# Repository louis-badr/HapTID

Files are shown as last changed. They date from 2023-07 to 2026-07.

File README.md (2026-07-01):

# HapTID - Haptic Technology for Improved Dexterity

<p align="center">
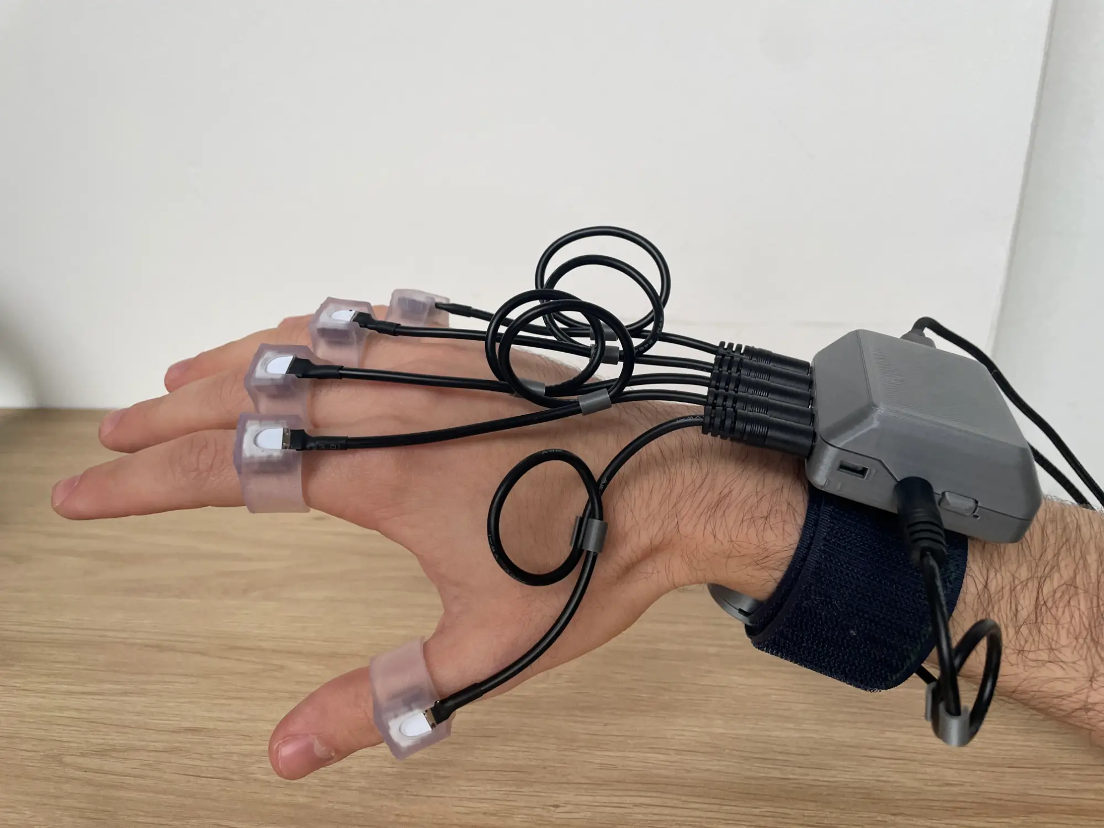
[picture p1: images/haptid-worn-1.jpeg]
HapTID device
  
</p>

HapTID is a study on how vibrotactile stimulation can improve manual dexterity in healthy subjects. In this repository you will find:

- Hardware :
    - The parts list and assembly guide of the device
    - CAD files for the 3D printed parts
    - Electronic schematics and PCB design files

- Software :
    - A pygame program for the study on healthy subjects
    - A script to generate the running order of the tasks and parameters for the study

- Firmware :
    - Arduino sketches for the study on healthy subjects
    - Arduino sketches to test motor vibrations using an accelerometer

You can also find a web interface to test the device at [https://louis-badr.fr/HapTID/](https://louis-badr.fr/HapTID/) and its source code in the `web_app` branch.

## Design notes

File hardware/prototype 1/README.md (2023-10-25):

# HapTID first hardware prototype

This folder contains the first hardware prototype of the HapTID project.
The design objectives of this prototype are:
- be able to produce sub-threshold vibrations on the wrist ranging from 0 to 500 Hz
- be able to produce supra-threshold vibrations on each finger
- be able to produce different signals simultaneously on all actuators
- has wired communication to reduce latency (this is an experimental prototype)

## Parts list
 
### 3D printed parts

The enclosures were printed with a Prusa i3 MK3S in PLA filament with 0.2 mm layer height and no supports.
The flexible rings can be casted in silicone with a 3D printed mold, here they were 3D printed with Formlabs Flexible 80A resin.
You can find the .step files in the `3D models` folder.

### Electronics

- Custom Prototype 1 PCB
- Generic ESP32 WROOM DevKit (38 pins)
- x6 2.5mm male audio jack connectors
- x6 VLV101040A motors by Vybronics
- x1 HD-VA3222 motor by PUI Audio

### Other parts

- A velcro strap (38mm wide here)
- x4 M2x8mm screws to secure the PCB

## Assembly guide

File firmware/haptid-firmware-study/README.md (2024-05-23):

# HapTID firmware

This is the Arduino sketch made to run for the study on healthy subjects (works with pygame_study_software).
The ESP32 listens to the serial port for a value:

- 0 to stop all vibrations

- between 1 and 100000 to control the noise level on output 1 (from 0.001% to 100%)

- between 100001 and 200000 to control the 80Hz tone level on ouput 3
- between 200001 and 300000 to control the 80Hz tone level on output 5
- between 300001 and 400000 to control the 250Hz tone level on output 3
- between 400001 and 500000 to control the 250Hz tone level on output 5

- between -1 and -100000 to control the click level on output 1
- between -100001 and -199999 to control the click level on output 2
- between -200001 and -299999 to control the click level on output 3
- between -300001 and -399999 to control the click level on output 4
- between -400001 and -499999 to control the click level on output 5
- between -500001 and -599999 to control the click level on output 6
- between -600001 and -699999 to control the click level for a click on all outputs at the same time

- between -700001 and -799999 to play a sine click on output 1
- between -800001 and -899999 to play a sine click on output 2
- between -900001 and -999999 to play a sine click on output 3
- between -1000001 and -1099999 to play a sine click on output 4
- between -1100001 and -1199999 to play a sine click on output 5
- between -1200001 and -1299999 to play a sine click on output 6

There is also a .wav file converter modified from https://github.com/rgrosset/pico-pwm-audio by Robin Grosset.

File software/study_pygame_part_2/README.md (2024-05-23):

# HapTID Study Part 2

## Goal: Assess the effects of sub-threshold wrist noise vibrations on reaction time

The main goal of this study is to assess the effects of wrist sub-threshold noise vibrations on reaction time.
The study is divided into three parts to:
1. Get the Stochastic Resonance (SR) vibration level by measuring the participant's Perception Threshold (PT) to noise at the wrist (set to 80% of the participant's PT)
2. Get the maximum finger vibration level (for confort) by assessing the participant's PT to 250Hz sinusoidal vibration on the index finger (set to 150% of the participant's PT)
3. Assess the effects of SR on reaction time with a Choice Reaction Time (CRT) task

## Setup
The participant is seated at a table in front of a computer screen, with the HapTID device installed on their non-dominant hand.
For the CRT task, each of their finger rests on a force sensitive button.
The participant wears earplugs to isolate them from the sounds the stimulators and the speaker can produce.

## Course of the study

### Perception Thresholds (approx. 6min)
To assess the participant's perceptual thresholds to different stimuli (1)(2), the double staircase method is used:
One after the other, a stimulus is emitted by the HapTID device.
The participant is asked to indicate whether or not they perceive the stimulus.
Depending on the response, the stimulus intensity is increased or decreased until a threshold is found.
Each assessment consists of a descending then ascending phase of stimulus intensity.

### Choice Reaction Time (CRT) task (33min45s without breaks)
The exercises are grouped by block according to the instructions (visual and/or tactile) and the presence or absence of sub-threshold wrist noise.
The exercises follow each other every 3 seconds.
The participant must press a key to continue, and can therefore take a break, every 25 exercises.
The course of the study is as follows:

1. Block without noise (sub-blocks in random order)(9x5x5x3 = 11min15s minimum):
    - No WS, visual IS, 5 repetitions per finger (random order)
    - No WS, tactile IS (click), 5 repetitions per finger (random order)
    - No WS, tactile IS (vibration), 5 repetitions per finger (random order)
    - Visual WS, visual IS, 5 repetitions per finger (random order)
    - Visual WS, tactile IS (click), 5 repetitions per finger (random order)
    - Visual WS, tactile IS (vibration), 5 repetitions per finger (random order)
    - Tactile WS (click), visual IS, 5 repetitions per finger (random order)  
    - Tactile WS (click), tactile IS (click), 5 repetitions per finger (random order)
    - Tactile WS (click), tactile IS (vibration), 5 repetitions per finger (random order)

2. Block with noise (sub-blocks identical to block 1 in random order)(11min15s minimum)

3. Control block without noise (sub-blocks identical to block 1 in random order)(11min15s minimum)

(WS: Warning Signal, IS: Imperative Signal)

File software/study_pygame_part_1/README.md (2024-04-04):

# HapTID Study Part 1

## Objectives
1. Get the Stochastic Resonance (SR) volume level by assessing the participant's perception threshold to white noise at the wrist
2. Assess the effects of SR on sensitivity (index finger) to
    1. 80Hz sinusoidal vibration
    2. 250Hz sinusoidal vibration
    3. Clicks

## Setup
The participant is seated at a table in front of a computer screen, with the HapTID device installed on his non-dominant hand. Their index finger rests on the surface of a bone-conduction audio speaker. The participant wears earplugs to isolate them from the sounds the stimulators and the speaker can produce.

## Course of the study
The study aims to assess the participant's perceptual thresholds to different stimuli.
The double staircase method is used: One after the other, a stimulus is emitted by the HapTID device or by the bone conduction loudspeaker. The participant is asked to indicate whether or not they perceive the stimulus. Depending on the response, the stimulus intensity is increased or decreased until a threshold is found. Each assessment consists of a descending then ascending phase of stimulus intensity.
Assessments are performed in the following order:
1. Assessment of white noise perception threshold on the wrist
2. Assessment of perception threshold on index finger without SR to (random order for each participant):
    - 80Hz sinusoidal vibration
    - 250Hz sinusoidal vibration
    - Clicks
3. Assessment of perception threshold on index finger with SR to (same order as previous assessment):
    - 80Hz sinusoidal vibration
    - 250Hz sinusoidal vibration
    - Clicks
4. Assessment of perception threshold on index finger without SR to (same order as previous assessment):
    - 80Hz sinusoidal vibration
    - 250Hz sinusoidal vibration
    - Clicks

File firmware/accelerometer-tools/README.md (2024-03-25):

# Accelerometer Sketches

The aim of using an accelerometer with vibration motors is to:
- Verify the latency of the system
- Analyze and equalize the frequency response of the motors

## Wiring

Using the ADXL345 accelerometer:

- VCC -> 3.3V
- GND -> GND
- X-OUT -> any input pin
- Y-OUT -> any input pin
- Z-OUT -> any input pin

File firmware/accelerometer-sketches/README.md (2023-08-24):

# Accelerometer Sketches

The aim of using an accelerometer with vibration motors is to:
- Verify the latency of the system
- Have the same vibration intensity for given frequencies

## Wiring

Using the ADXL345 accelerometer:

VCC -> 3.3V
GND -> GND
X-OUT -> any input pin
Y-OUT -> any input pin
Z-OUT -> any input pin

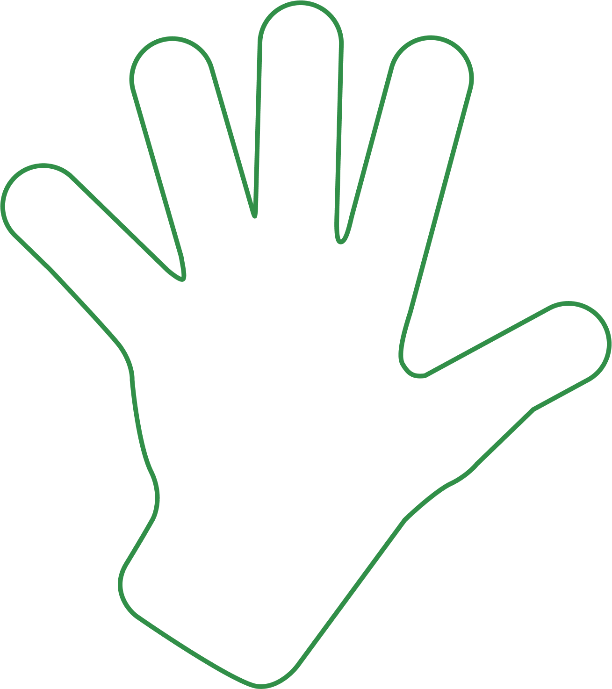
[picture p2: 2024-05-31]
software/study_pygame_part_2/hand_drawing_green.png

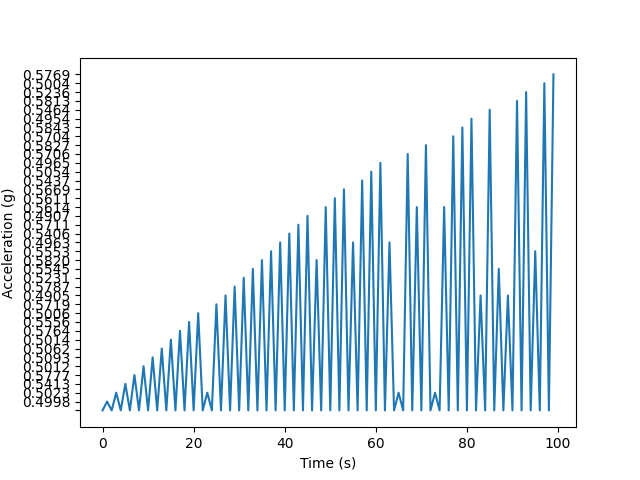
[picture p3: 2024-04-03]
firmware/accelerometer-tools/Figure_1.png

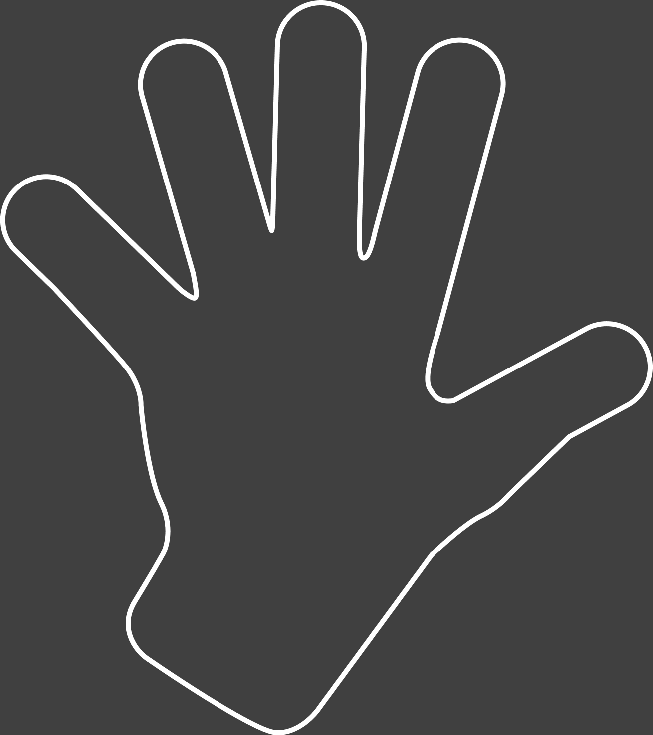
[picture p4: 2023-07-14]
software/study_pygame_part_2/hand_drawing.png

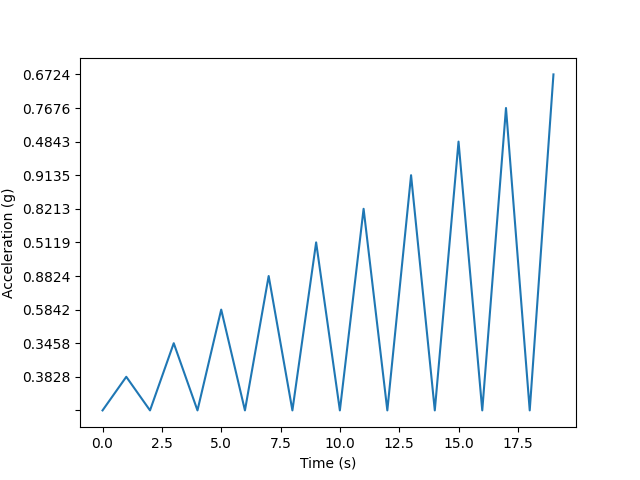
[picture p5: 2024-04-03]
firmware/accelerometer-tools/Figure_2.png

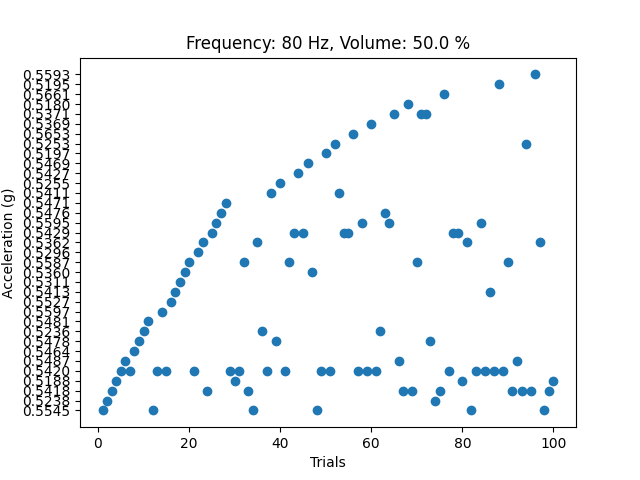
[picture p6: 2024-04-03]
firmware/accelerometer-tools/Figure_3.png

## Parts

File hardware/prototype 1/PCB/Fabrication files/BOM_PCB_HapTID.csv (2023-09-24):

ID | Name | Designator | Footprint | Quantity | Manufacturer Part | Manufacturer | Supplier | Supplier Part | Price
1 | PJ-2104-3A | #1,#2,#3,#4,#5,#6 | AUDIO-TH_PJ-2104-3A | 6 | PJ-2104-3A | Korean Hroparts Elec | LCSC | C707243 | 0.094
2 | 560 | R22 | R0603 | 1
3 | 300 | R23 | R0603 | 1
4 | KT-0603R | LED1 | LED0603-RD | 1 | KT-0603R | KENTO | LCSC | C2286
5 | 19-217/GHC-YR1S2/3T | LED2 | LED0603-RD | 1 | 19-217/GHC-YR1S2/3T | EVERLIGHT(亿光) | LCSC | C72043 | 0.027
6 | TYPE-C 6P(073) | USB1 | TYPE-C-SMD_TYPE-C-6P | 1 |  | SHOU HAN(首韩) | LCSC | C668623 | 0.039
7 | 56n | C1,C5,C11,C15,C21,C25 | C0603 | 6
8 | 5.6n | C2,C6,C12,C16,C22,C26 | C0603 | 6
9 | 1u | C3,C4,C7,C8,C13,C14,C17,C18,C23,C24,C27,C28 | C0603 | 12
10 | 3.9k | R1,R3,R8,R10,R15,R17 | R0603 | 6
11 | 39k | R2,R4,R9,R11,R16,R18 | R0603 | 6
12 | 10k | R5,R12,R19 | R0603 | 3
13 | 100k | R6,R7,R13,R14,R20,R21 | R0603 | 6
14 | 0.1u | C10,C20,C30 | C0603 | 3
15 | XKB5858-Z-C | SW1 | SW-TH_XKB5858-Z-C | 1 | XKB5858-Z-C | XKB Connectivity(中国星坤) | LCSC | C318865 | 0.178
16 | MAX98306ETD+T | U1,U2,U3 | TDFN-14_L3.0-W3.0-P0.40-BL-EP | 3 | MAX98306ETD+T | ADI(亚德诺)/MAXIM(美信) | LCSC | C124549 | 2.746
17 | 100u | C9,C19,C29 | C1206 | 3

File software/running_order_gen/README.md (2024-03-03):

# Running order generation script

This is a script to generate a running order for the HapTID experiment.

## Déroulement de l'étude :

1. Calibration pour la résonance stochastique par mesure du seuil de perception aux vibrations stochastiques

2. Mesure du seuil de perception aux vibrations sur l'index sans et avec vibrations stochastiques (sans, avec puis sans pour contrôle)

3. Exercices (1h18min45s sans pauses)

Deux types d'exercices sont à réaliser: de temps de réaction à choix (noté CRT) ou de contrôle isométrique de la force avec l'index (noté FC).
L'ordre des exercices est aléatoire.

### Exercices de temps de réaction à choix (CRT):

Les exercices sont groupés par bloc selon les instructions (visuelles et/ou tactiles) et la présence ou non de vibrations stochastiques.
Les exercices s'enchaînent toutes les 3 secondes.
Le sujet doit appuyer sur une touche pour continuer et peut donc prendre une pause tous les 25 exercices.
Le déroulement est le suivant:

1. Bloc sans vibrations stochastiques (sous-blocs en ordre aléatoire)(9x5x5x3 = 11min15s minimum):
    - Pas de WS, IS visuel, 5 répétitions par doigt (ordre aléatoire)
    - Pas de WS, IS tactile (click), 5 répétitions par doigt (ordre aléatoire)
    - Pas de WS, IS tactile (vibration), 5 répétitions par doigt (ordre aléatoire)
    - WS visuel, IS visuel, 5 répétitions par doigt (ordre aléatoire)
    - WS visuel, IS tactile (click), 5 répétitions par doigt (ordre aléatoire)
    - WS visuel, IS tactile (vibration), 5 répétitions par doigt (ordre aléatoire)
    - WS tactile (click), IS visuel, 5 répétitions par doigt (ordre aléatoire)  
    - WS tactile (click), IS tactile (click), 5 répétitions par doigt (ordre aléatoire)
    - WS tactile (click), IS tactile (vibration), 5 répétitions par doigt (ordre aléatoire)

2. Bloc avec vibrations stochastiques (sous-blocs identiques au bloc 1 en ordre aléatoire)(11min15s minimum)

3. Bloc contrôle sans vibrations stochastiques (sous-blocs identiques au bloc 1 en ordre aléatoire)(11min15s minimum)

(WS: Warning Signal, IS: Imperative Signal)

### Exercices de contrôle isométrique de la force de l'index (FC):

Les exercices sont groupés par bloc selon les instructions (visuelles et/ou tactiles) et la présence ou non de vibrations stochastiques.
Le sujet doit appuyer sur une touche pour continuer et peut donc prendre une pause entre chaque exercice.
Le déroulement est le suivant:

1. Bloc sans vibrations stochastiques (sous-blocs en ordre aléatoire)(6x5x30 = 15min minimum):
    - Force target à 4N, instruction visuelle, 5 répétitions
    - Force target à 6N, instruction visuelle, 5 répétitions
    - Force target à 8N, instruction visuelle, 5 répétitions
    - Force target à 4N, instruction tactile, 5 répétitions
    - Force target à 6N, instruction tactile, 5 répétitions
    - Force target à 8N, instruction tactile, 5 répétitions

2. Bloc avec vibrations stochastiques (sous-blocs identiques au bloc 1 en ordre aléatoire)(15min minimum)

3. Bloc contrôle sans vibrations stochastiques (sous-blocs identiques au bloc 1 en ordre aléatoire)(15min minimum)

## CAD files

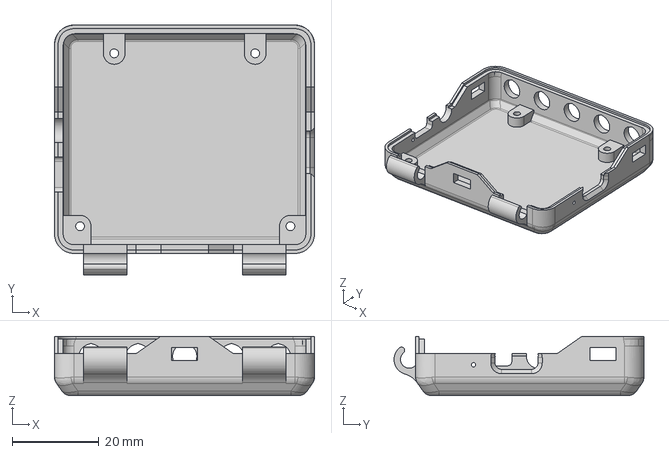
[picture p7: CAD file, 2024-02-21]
hardware/prototype 1/3D models/electronics_enclosure_bottom_w_clips.step
60.0 x 57.7 x 13.7 mm

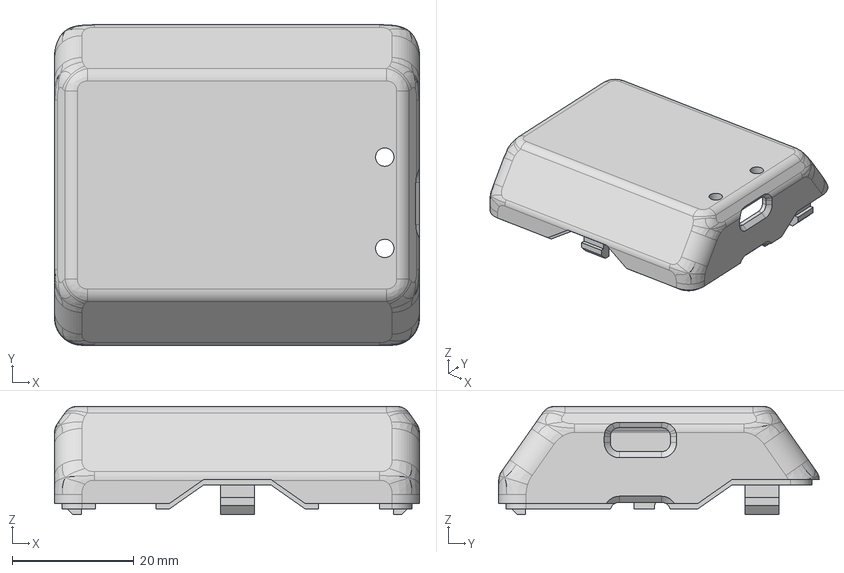
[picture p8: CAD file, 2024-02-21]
hardware/prototype 1/3D models/electronics_enclosure_top_w_holes.step
60.0 x 52.7 x 17.8 mm

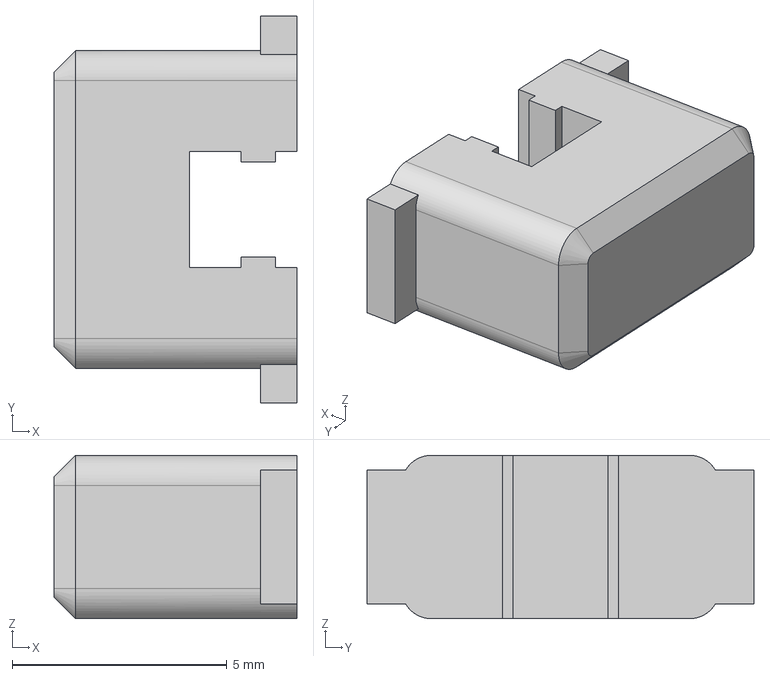
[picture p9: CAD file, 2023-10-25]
hardware/prototype 1/3D models/electronics_enclosure_button.step
5.65 x 9.00 x 3.80 mm

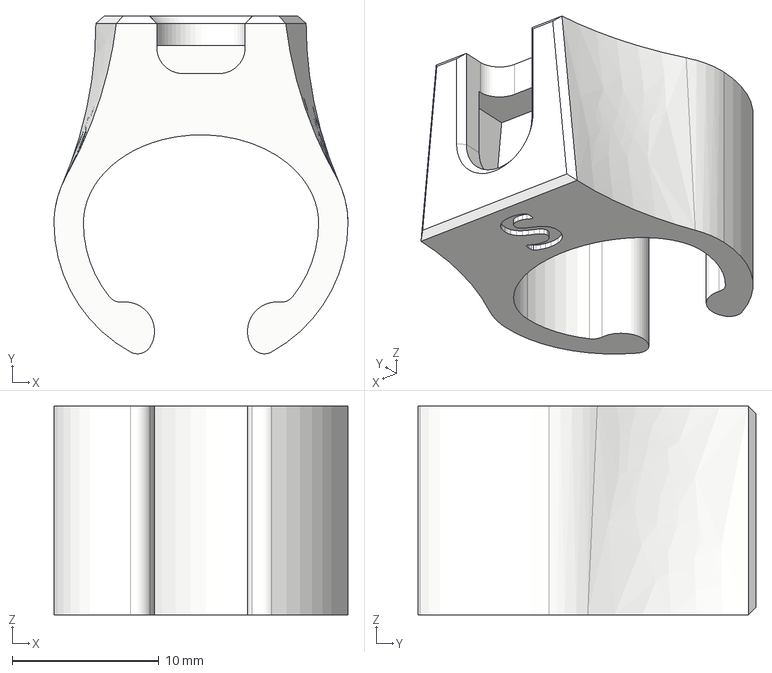
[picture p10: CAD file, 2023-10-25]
hardware/prototype 1/3D models/motor_ring_small.step
20.0 x 23.0 x 14.2 mm

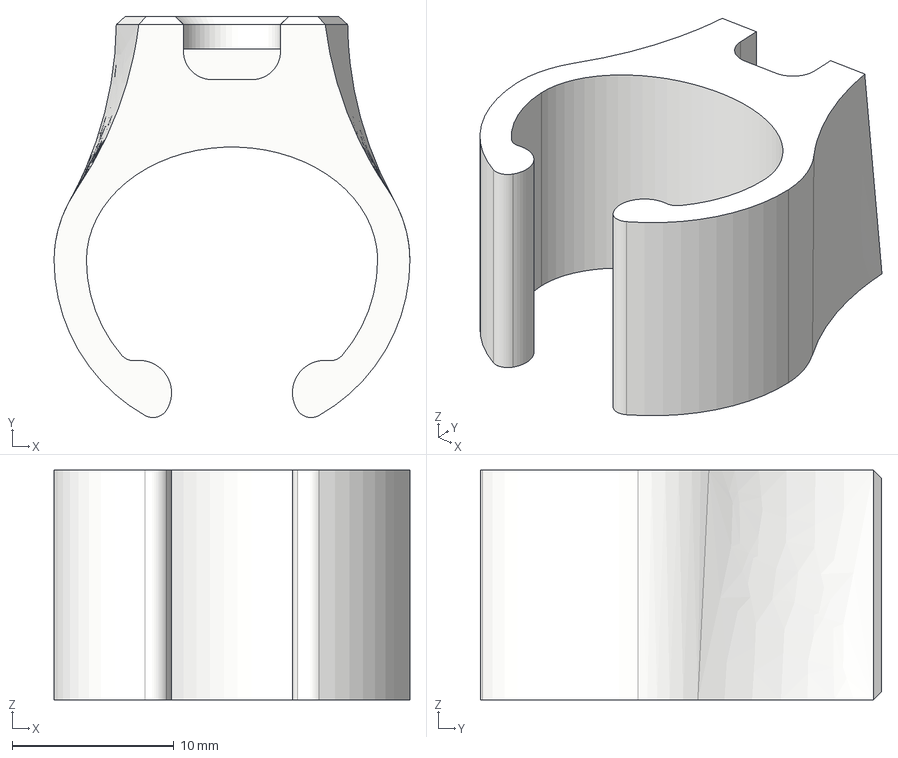
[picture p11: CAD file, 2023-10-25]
hardware/prototype 1/3D models/motor_ring_medium.step
22.0 x 24.8 x 14.2 mm

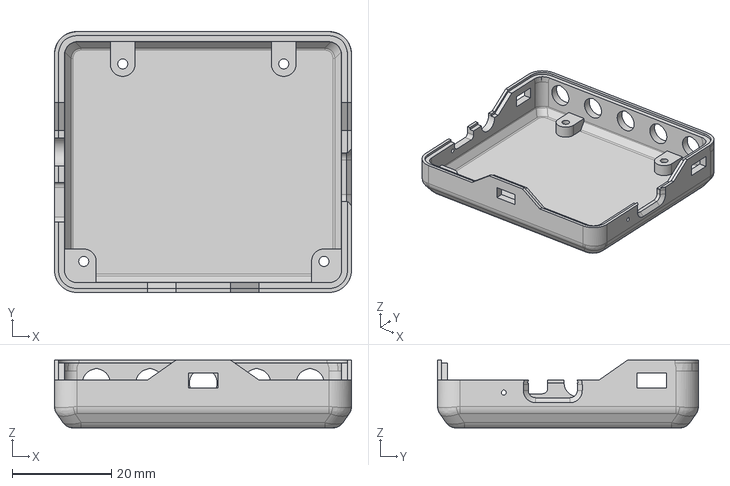
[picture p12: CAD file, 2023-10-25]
hardware/prototype 1/3D models/electronics_enclosure_bottom.step
60.0 x 52.7 x 13.7 mm

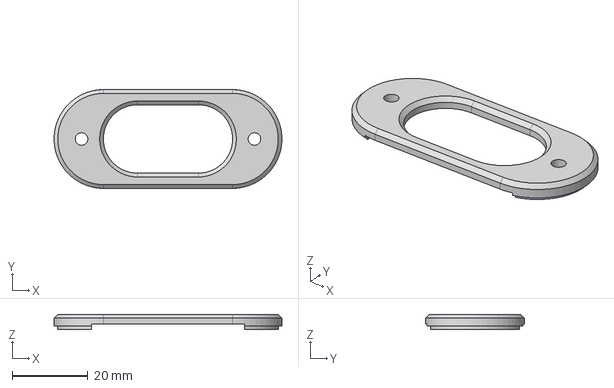
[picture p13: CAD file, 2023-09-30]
hardware/prototype 1/3D models/wrist_motor_enclosure_top.step
60.0 x 26.0 x 4.00 mm

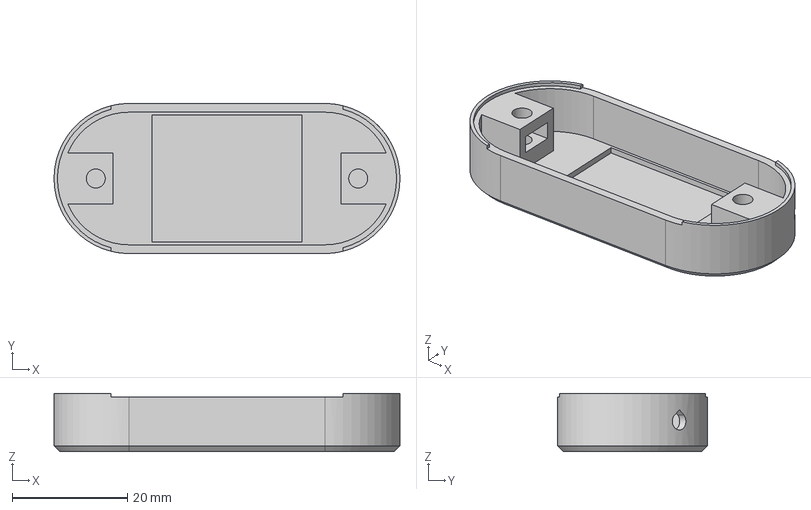
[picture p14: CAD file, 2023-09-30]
hardware/prototype 1/3D models/wrist_motor_enclosure_bottom.step
60.0 x 26.0 x 10.1 mm

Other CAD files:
hardware/prototype 1/3D models/electronics_enclosure_top.step

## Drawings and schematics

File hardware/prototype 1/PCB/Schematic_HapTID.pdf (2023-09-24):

## FILTERS + AMPS

## ESP32 WROOM GENERIC DEVKIT

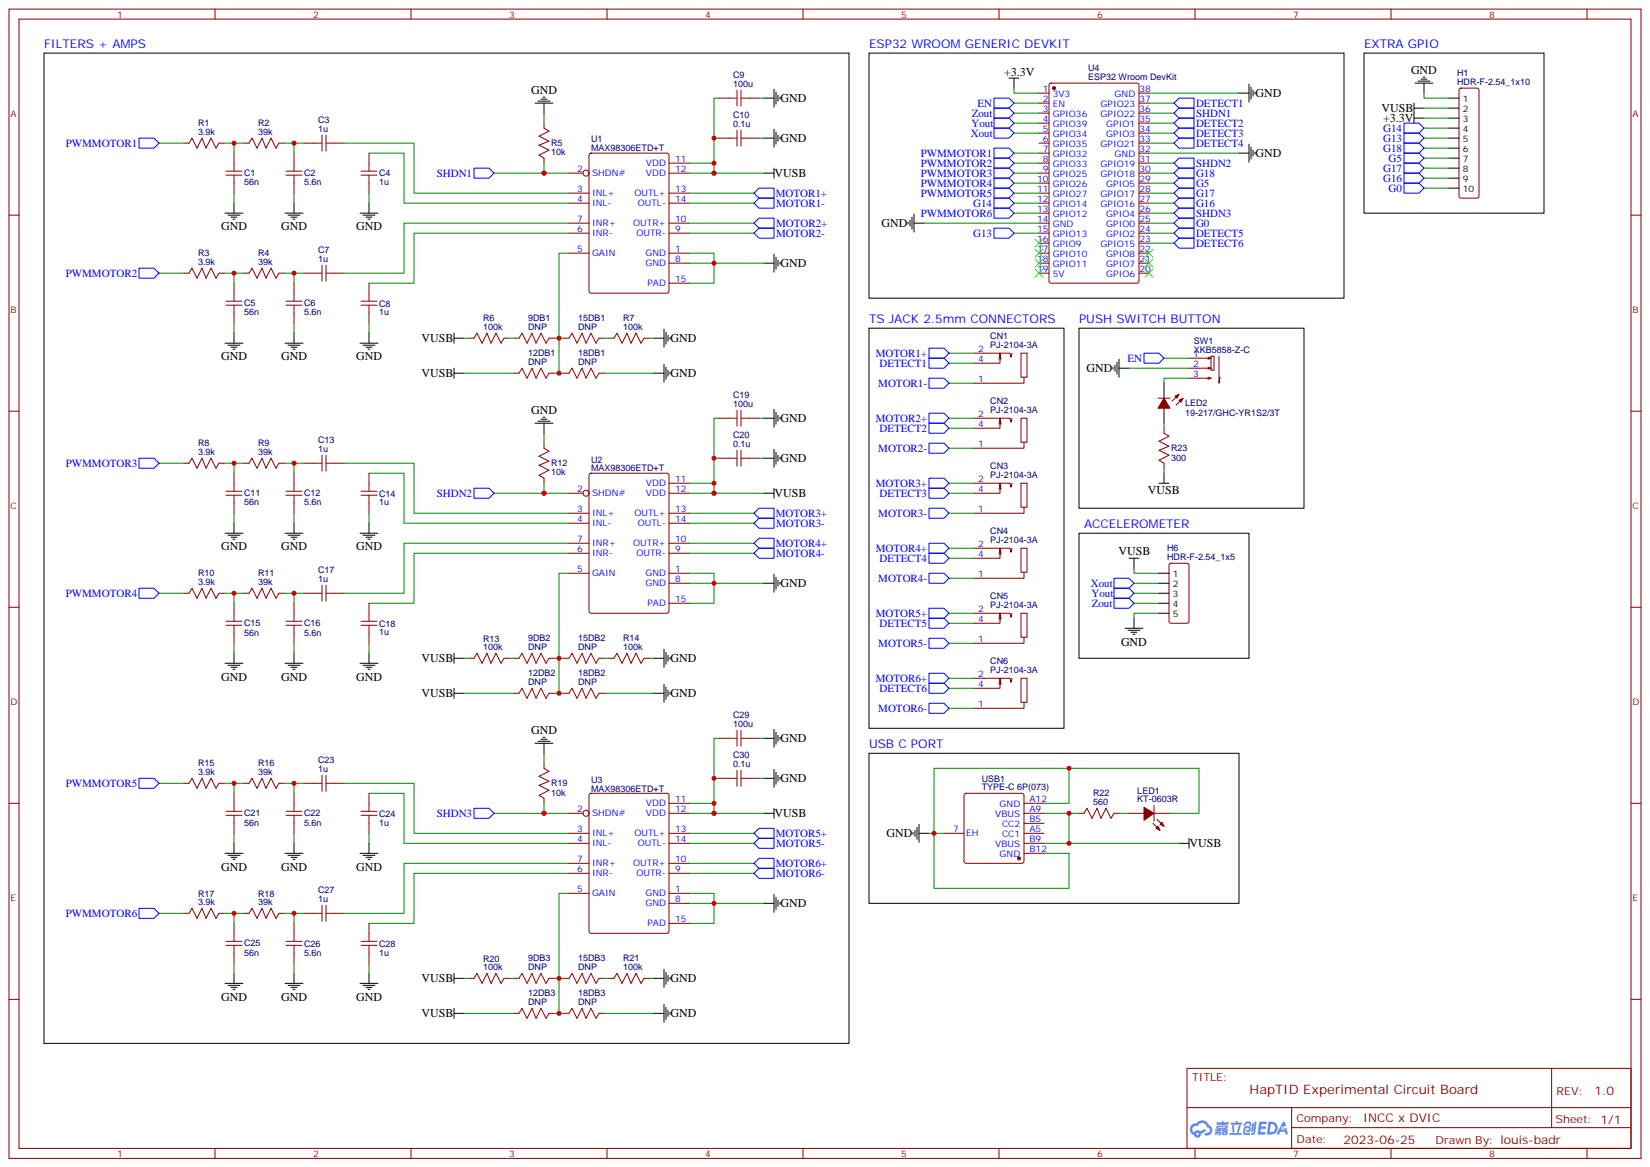
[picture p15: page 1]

Drawn By: louis-badr

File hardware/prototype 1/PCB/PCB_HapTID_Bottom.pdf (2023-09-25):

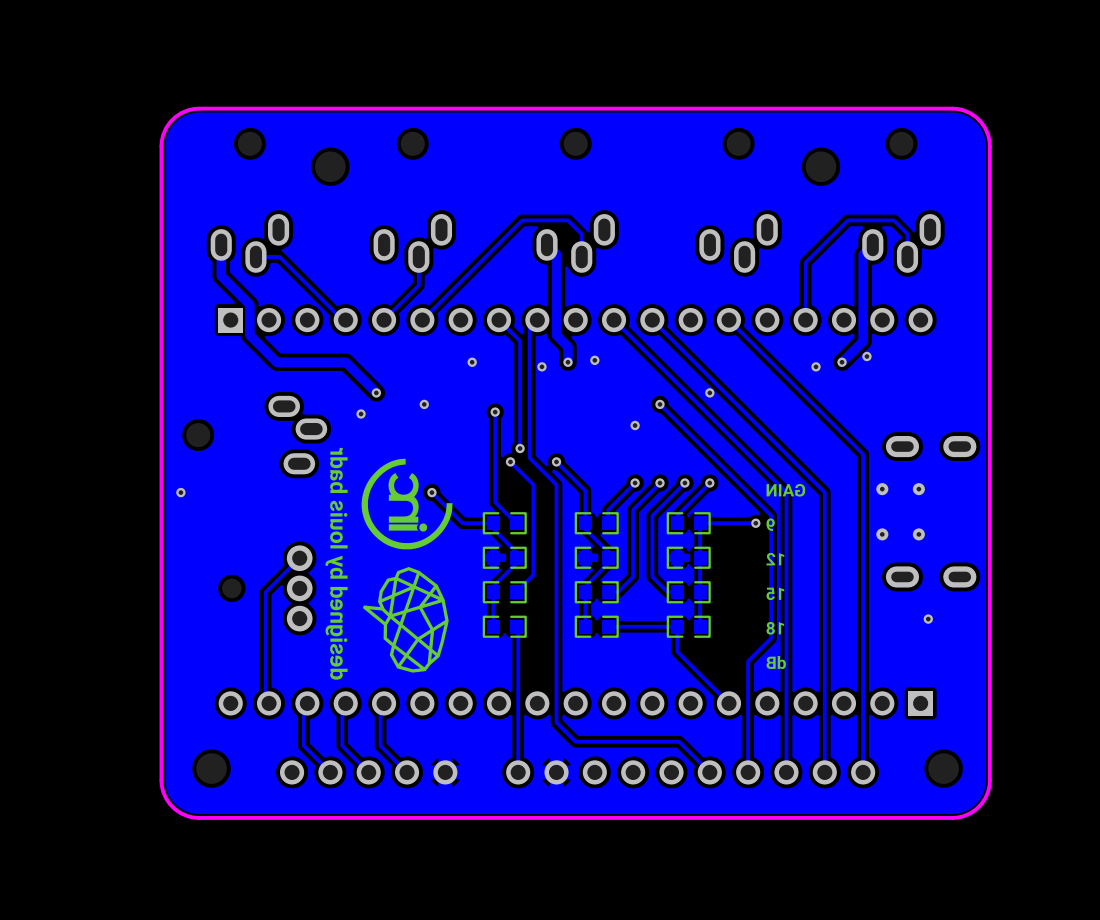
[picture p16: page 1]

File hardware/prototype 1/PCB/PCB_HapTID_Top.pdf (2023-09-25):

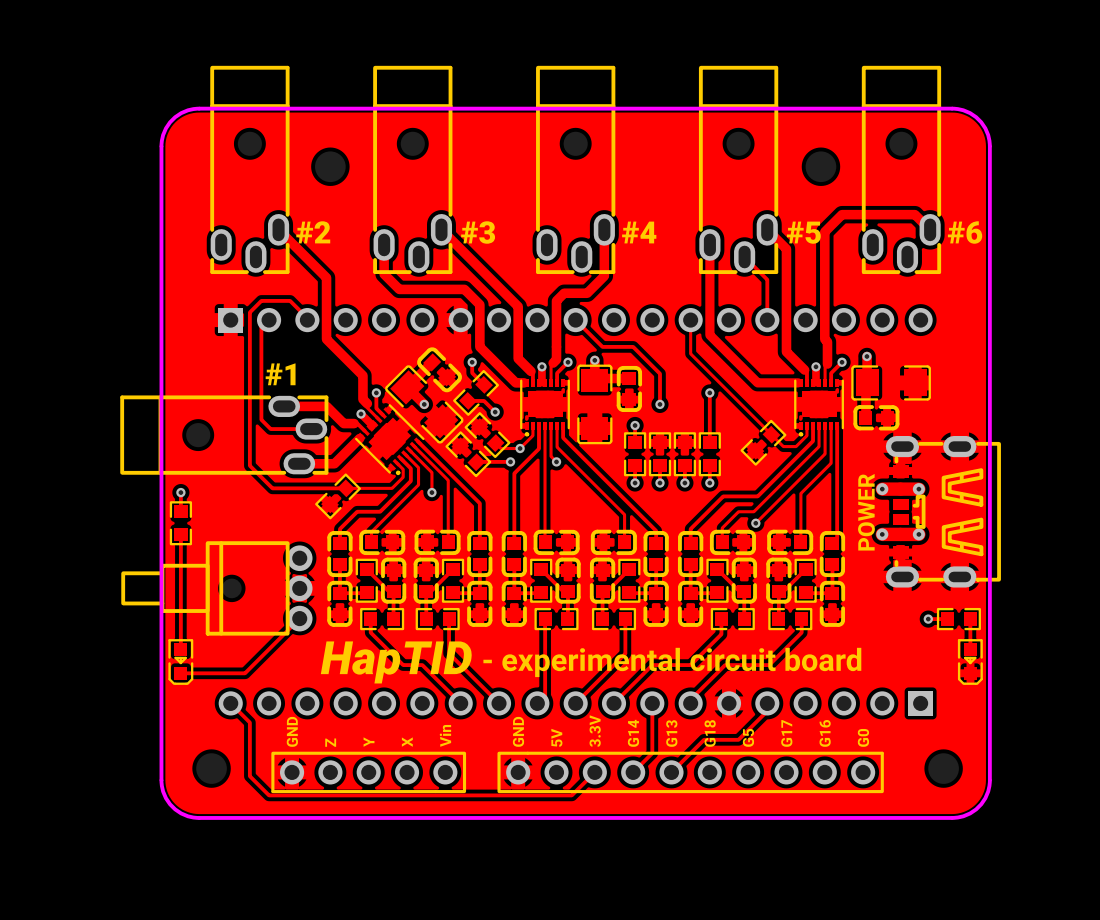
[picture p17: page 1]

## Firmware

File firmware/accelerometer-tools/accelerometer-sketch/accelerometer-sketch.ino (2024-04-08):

#include <Arduino.h>

const int adcResolution = 10;
const float adcRange = pow(2, adcResolution) - 1;

const int xPin = A12;
const int yPin = A11;
const int zPin = A10;

// Number of samples for readAxis
const int sampleSize = 100;

// Rest values for each axis
float xRest = 0, yRest = 0, zRest = 0;

bool streaming = false;
bool centered = false;

struct axesVal
{
  float x;
  float y;
  float z;
};

// Read the value of each axis at rest (average of sampleSize samples)
int readSampleAxis(int axisPin)
{
  long reading = 0;
  for (int i = 0; i <= sampleSize; i++)
  {
    reading += analogRead(axisPin);
  }
  return reading/sampleSize;
}

// Calibrate all axes by reading the value at rest
axesVal calibrateAllAxes()
{
  // Serial.println("Calibration started");
  // for each axis read the value at rest
  xRest = readSampleAxis(xPin);
  yRest = readSampleAxis(yPin);
  zRest = readSampleAxis(zPin);
  // convert raw values to G between -3 and 3 G (ADXL335)
  xRest = (xRest / adcRange) * 6.0 - 3.0;
  yRest = (yRest / adcRange) * 6.0 - 3.0;
  zRest = (zRest / adcRange) * 6.0 - 3.0;
  // Serial.println("Calibration Done");
  return {xRest, yRest, zRest};
}

// Read raw value of all axes
axesVal readAllAxesRaw()
{
  // read raw values
  float xRaw = analogRead(xPin);
  float yRaw = analogRead(yPin);
  float zRaw = analogRead(zPin);
  return {xRaw, yRaw, zRaw};
}

// Read raw value of all axes
axesVal readAllAxesRawSamples()
{
  // read raw values
  float xRaw = readSampleAxis(xPin);
  float yRaw = readSampleAxis(yPin);
  float zRaw = readSampleAxis(zPin);
  return {xRaw, yRaw, zRaw};
}

// Read the value of all axes in G
axesVal readAllAxesG()
{
  axesVal axesRaw = readAllAxesRaw();
  // convert raw values to G between -3 and 3 G (ADXL335)
  float xG = (axesRaw.x / adcRange) * 6.0 - 3.0;
  float yG = (axesRaw.y / adcRange) * 6.0 - 3.0;
  float zG = (axesRaw.z / adcRange) * 6.0 - 3.0;
  return {xG, yG, zG};
}

// Read the value of all axes in G
axesVal readAllAxesGSamples()
{
  axesVal axesRaw = readAllAxesRawSamples();
  // convert raw values to G between -3 and 3 G (ADXL335)
  float xG = (axesRaw.x / adcRange) * 6.0 - 3.0;
  float yG = (axesRaw.y / adcRange) * 6.0 - 3.0;
  float zG = (axesRaw.z / adcRange) * 6.0 - 3.0;
  return {xG, yG, zG};
}

// Read the value of all axes centered on rest value
axesVal readAllAxesCentered()
{
  axesVal axesG = readAllAxesG();
  // center values
  float xCentered = axesG.x - xRest;
  float yCentered = axesG.y - yRest;
  float zCentered = axesG.z - zRest;
  return {xCentered, yCentered, zCentered};
}

// Print the value of all axes
void printAllAxes(axesVal axesVal)
{
  Serial.print(.25);
  Serial.print(",");
  Serial.print(-0.25);
  Serial.print(",");
  //Serial.print("xG:");
  Serial.print(axesVal.x, 4);
  Serial.print(",");
  //Serial.print("yG:");
  Serial.print(axesVal.y, 4);
  Serial.print(",");
  //Serial.print("zG:");
  Serial.println(axesVal.z, 4);
}

// Read acceleration on all axes
float readAcceleration(axesVal axesVal)
{
  return sqrt(pow(axesVal.x, 2) + pow(axesVal.y, 2) + pow(axesVal.z, 2));
}


void setup() 
{
  //Serial.begin(38400);
  analogReadResolution(adcResolution);
}

void loop() 
{
  if (Serial.available() > 0) 
  {
    char incomingByte = Serial.read();
    // Serial.print("Received : ");
    // Serial.println(incomingByte);

    // Calibration
    if((int)incomingByte == '1')
    {
      calibrateAllAxes();
    }
    // Start or stop streaming G value of all axis
    if((int)incomingByte == '2')
    {
      if(streaming)
      {
        streaming = false;
        centered = false;
        Serial.println("Streaming G values stopped\n");
      }
      else
      {
        streaming = true;
        Serial.println("Streaming G values started\n");
      }
    }
    // Start or stop streaming centered G value of all axis - please run the calibration first
    if((int)incomingByte == '3')
    {
      if(streaming)
      {
        streaming = false;
        centered = false;
        Serial.println("Streaming centered values stopped\n");
      }
      else
      {
        streaming = true;
        centered = true;
        Serial.println("Streaming centered values started\n");
      }
    }
    // Read acceleration
    if((int)incomingByte == '4')
    {
      // Serial.print("Acceleration:");
      Serial.print(readAllAxesRawSamples().z, 4);
    }
  }

  if (streaming)
  {
    if(centered)
    {
      printAllAxes(readAllAxesCentered());
    }
    else
    {
      // printAllAxes(readAllAxesG());
      Serial.print(readAcceleration(readAllAxesRaw()), 4);
      // add a min and max value for the plot
      Serial.print(",");
      Serial.print(900);
      Serial.print(",");
      Serial.println(950);

    }
    delay(20);
  }
}

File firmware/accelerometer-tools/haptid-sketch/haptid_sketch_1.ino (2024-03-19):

#include "Arduino.h"

const int pwmRes = 12;
const int sampleRate = 16000;

const int shdnPins[3] = {22, 19, 4};  // keep pin on HIGH to run the amp - each amp controls two motors
const int motorPins[6] = {32, 33, 25, 26, 27, 12};  // in order from left to right

const int pwmMax = pow(2, pwmRes) - 1;
const int pwmFreq = (8 * pow(10, 7)) / pow(2, pwmRes);  // 80 MHz / 2^13 = 9765.625 Hz > sampleRate

hw_timer_t * timer = NULL;

uint16_t sineTable[sampleRate] = {0};
int arrayPosition = 0;
int arrayLength = 0;

void playStartSequence()
{
  for (int i = 0; i <= 5; i++)
  {
    ledcWrite(i, 0);
    ledcWrite(i, pwmMax);
    delay(7);
    ledcWrite(i, 0);
    delay(250);
  }
  delay(500); 
  // do it in reverse
  for (int i = 5; i >= 0; i--)
  {
    ledcWrite(i, 0);
    ledcWrite(i, pwmMax);
    delay(7);
    ledcWrite(i, 0);
    delay(250);
  }
}


// Interrupt function to play the signals
void IRAM_ATTR onTimer()
{
  if (receivedValue > 0)
  {
    if (arrayPosition < arrayLength)
    {
      ledcwWrite(0, sineTable[arrayPosition]);
      arrayPosition++;
    }
    else
    {
      arrayPosition = 0;
    }
  }
}

void setup()
{
  Serial.begin(115200);
  Serial.setTimeout(1);
  // Serial.print("APB Freq = ");
  // Serial.print(getApbFrequency());
  // Serial.println(" Hz");
  // init shdn pins and turn on amps
  for (int i = 0; i <= 2; i++)
  {
    pinMode(shdnPins[i], OUTPUT);
    digitalWrite(shdnPins[i], HIGH);
  }
  // init motor pins
  for (int i = 0; i <= 5; i++)
  {
    ledcSetup(i, pwmFreq, pwmRes);
    ledcAttachPin(motorPins[i], i);
  }
  // init interrupt timer
  timer = timerBegin(0, 80, true);
  timerAttachInterrupt(timer, &onTimer, true);
  timerAlarmWrite(timer, 1000000 / sampleRate, true);  // nombre de us (1 000 000 us = 1s pour rappel)
  timerAlarmEnable(timer);
  
  delay(2000);
  playStartSequence();
}

void loop()
{
  if (Serial.available() > 0)
  {
    int receivedValue = Serial.parseInt();
    Serial.print("Received: ");
    Serial.println(receivedValue);
    if (receivedValue > 0 && receivedValue <= 20000)
    {
      arrayLength = sampleRate / receivedValue;
      // clear the old sine table
      for (int i = 0; i < arrayLength; i++)
      {
        sineTable[i] = 0;
      }
      // generate a new sine table
      for (int i = 0; i < arrayLength; i++)
      {
        sineTable[i] = (uint16_t)(sin(2 * PI * i / arrayLength) * pwmMax / 2 + pwmMax / 2);
      }
      Serial.print("Playing tone at ");
      Serial.print(receivedValue);
      Serial.println(" Hz");
    }
    else if (receivedValue == 0)
    {
      for (int i = 0; i <= 5; i++)
      {
        ledcWrite(i, 0);
      }
      Serial.println("Stopping tone");
    }
    else
    {
      Serial.println("Invalid value");
    }
  }
}

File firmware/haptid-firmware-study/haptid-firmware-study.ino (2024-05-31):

#include <Arduino.h>
#include "whitenoise.h"

const int shdnPins[3] = {22, 19, 4};  // keep pin on HIGH to run the amp - each amp controls two motors
const int motorPins[6] = {32, 33, 25, 26, 27, 12};  // in order from left to right

const int pwmRes = 13;
const int sampleRate = 8000;
const int pwmMax = pow(2, pwmRes) - 1;
const int pwmFreq = (8 * pow(10, 7)) / pow(2, pwmRes);  // 80 MHz / 2^12 = 19531.25 Hz > sampleRate

hw_timer_t * timer = NULL;  // we only need one timer since the sample rate is the same for all sounds

const int clickDuration = 10;  // length of the click in ms
const int sineClickDuration = 50; // length of the sine click in ms
int sineClickArrayPosition = 0;  // position for the sine click - the length of the array is fixed
int wristArrayPosition = 0;  // position in the array being played
int fingerArrayPosition = 0;
int fingerArrayLength = 0;  // length of the array being played

int receivedValue = 0;  // value received from the serial port
int wristValue = 0;
int fingerValue = 0;

int clickOutput = -1;
int clickVolume;
int sineClickOutput = -1;
int sineClickVolume;
unsigned long clickTimer = 0;

// Debugging function to print an array
void printArray(uint16_t arr[], int size) {
  for (int i = 0; i < size; i++) {
    Serial.print(arr[i]);
    Serial.print(" ");
  }
  Serial.println();
}

// Generates a sine table at a given frequency and sample rate
uint16_t* generateSineTable(int frequency, int sampleRate)
{
  int samplesPerPeriod = sampleRate / frequency;
  uint16_t* sineTable = new uint16_t[samplesPerPeriod];
  for (int i = 0; i < samplesPerPeriod; i++)
  {
    sineTable[i] = (uint16_t)(sin(2 * PI * i / samplesPerPeriod) * pwmMax / 2 + pwmMax / 2);
  }
  return sineTable;
}

int sineTable80Length = sampleRate / 80;
int sineTable250Length = sampleRate / 250;
uint16_t* sineTable80 = generateSineTable(80, sampleRate); // 80 Hz sine wave for the motor on the index finger
uint16_t* sineTable250 = generateSineTable(250, sampleRate); // 250 Hz sine wave for the sine click

// Interrupt function to play the noise and the sine waves
void IRAM_ATTR onTimer()
{
  if (wristValue > 0 && wristValue <= 100000)
  {
    ledcWrite(0, whitenoise_data[wristArrayPosition] * wristValue / 100000);
    wristArrayPosition++;
    if (wristArrayPosition >= whitenoise_length)
    {
      wristArrayPosition = 0;
    }
  }
  if (fingerValue > 0)
  {
    if (fingerValue <= 200000)
    {
      ledcWrite(2, sineTable80[fingerArrayPosition] * (fingerValue - 100000) / 100000);
    } else if (fingerValue <= 300000)
    {
      ledcWrite(4, sineTable80[fingerArrayPosition] * (fingerValue - 200000) / 100000);
    } else if (fingerValue <= 400000)
    {
      ledcWrite(2, sineTable250[fingerArrayPosition] * (fingerValue - 300000) / 100000);
    } else if (fingerValue <= 500000)
    {
      ledcWrite(4, sineTable250[fingerArrayPosition] * (fingerValue - 400000) / 100000);
    } else if (fingerValue <= 600000)
    {
      ledcWrite(4, sineTable250[fingerArrayPosition] * (fingerValue - 500000) / 100000);
    }
    fingerArrayPosition++;
    if(fingerArrayPosition >= fingerArrayLength)
    {
      fingerArrayPosition = 0;
    }
  }
  if (sineClickVolume > 0)
  {
    if (sineClickArrayPosition < sineTable250Length)
    {
      ledcWrite(sineClickOutput, sineTable250[sineClickArrayPosition] * sineClickVolume / 100000.0);
      sineClickArrayPosition++;
    } else
    {
      sineClickArrayPosition = 0;
    }
  }
}

void playStartSequence()
{
  for (int i = 0; i <= 5; i++)
  {
    ledcWrite(i, 0);
    ledcWrite(i, pwmMax);
    delay(7);
    ledcWrite(i, 0);
    delay(250);
  }
  delay(500); 
  // do it in reverse
  for (int i = 5; i >= 0; i--)
  {
    ledcWrite(i, 0);
    ledcWrite(i, pwmMax);
    delay(7);
    ledcWrite(i, 0);
    delay(250);
  }
}

void setup()
{
  Serial.begin(115200);
  Serial.setTimeout(1);
  // Serial.print("APB Freq = ");
  // Serial.print(getApbFrequency());
  // Serial.println(" Hz");
  // init shdn pins and turn on amps
  for (int i = 0; i <= 2; i++)
  {
    pinMode(shdnPins[i], OUTPUT);
    digitalWrite(shdnPins[i], HIGH);
  } 
  // init motor pins
  for (int i = 0; i <= 5; i++)
  {
    ledcSetup(i, pwmFreq, pwmRes);
    ledcAttachPin(motorPins[i], i);
  }
  // init interrupt timer
  timer = timerBegin(0, 80, true);
  timerAttachInterrupt(timer, &onTimer, true);
  timerAlarmWrite(timer, 1000000 / sampleRate, true);  // nombre de us (1 000 000 us = 1s pour rappel)
  timerAlarmEnable(timer);
  delay(2000);
  playStartSequence();
  delay(1000);
}

void loop()
{
  if (Serial.available() > 0)
  {
    receivedValue = Serial.parseInt();
    Serial.print("Received Value: ");
    Serial.println(receivedValue);
    if (receivedValue == 0)
    {
      wristValue = 0;
      fingerValue = 0;
      for (int i = 0; i <= 5; i++)
      {
        ledcWrite(i, 0);
      }
    } else if (receivedValue < 0)  // -1 to -700000 are clicks, -700001 to -1300000 are sine clicks
    {
      if (receivedValue < -700000){
        sineClickOutput = -receivedValue/100000 - 7;
        sineClickVolume = -receivedValue % 100000;
        sineClickArrayPosition = 0;
      } else
      {
        clickOutput = -receivedValue/100000;
        clickVolume = -receivedValue % 100000;
        if (clickOutput != 6)
        {
          ledcWrite(clickOutput, 0);
          ledcWrite(clickOutput, pwmMax * clickVolume / 100000.0);
        } else
        {
          for (int i = 1; i <= 5; i++)
          {
            ledcWrite(i, 0);
            ledcWrite(i, pwmMax * clickVolume / 100000.0);
          }
        }
      }
      // set the click time
      clickTimer = millis();
    } else 
    {
      if (receivedValue <= 100000)
      {
        wristValue = receivedValue;
        wristArrayPosition = 0;
      } else if (receivedValue <= 300000)
      {
        fingerValue = receivedValue;
        fingerArrayPosition = 0;
        fingerArrayLength = sineTable80Length;
      } else if (receivedValue <= 500000)
      {
        fingerValue = receivedValue;
        fingerArrayPosition = 0;
        fingerArrayLength = sineTable250Length;
      }
    }
  }
  // if the motor is clicking
  if (clickOutput != 0)
  {
    // if more than X ms have passed since the click
    if (millis() - clickTimer >= clickDuration)
    {
      // turn off the motor
      if (clickOutput != 6)
      {
        ledcWrite(clickOutput, 0);
      } else
      {
        for (int i = 1; i <= 5; i++)
        {
          ledcWrite(i, 0);
        }
      }
      // set the motor to not clicking
      clickOutput = -1;
      clickVolume = 0;
    }
  }
  // if the motor is sine clicking
  if (sineClickOutput != -1)
  {
    if (millis() - clickTimer >= sineClickDuration)
    {
      // turn off the motor
      ledcWrite(sineClickOutput, 0);
      // set the motor to not clicking
      sineClickOutput = -1;
      sineClickVolume = 0;
    }
  }
}

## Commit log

2023-06-30 Calibration screen progress
2023-07-12 Refactoring to separate screens in different files
    [01BL-calibration.csv]
2023-07-14 Force control exercice progress
    [01BL-calibration.csv]
2023-07-15 Running order table added
    [running_order_table.csv]
2023-07-17 Progress functional CRT
    [running_order_table.csv]
2023-08-06 Running order generator first commit
    [01BL-calibration.csv, running_order.csv, running_order_table.csv]
2023-08-08 Running order gen tweaks
    [running_order.csv, running_order_table.csv]
2023-08-09 Firmware first commit
    [running_order.csv]
2023-09-12 Tweak running order gen
    [running_order_table.csv]
2023-09-12 Study soft progress
    [running_order_table.csv]
2023-09-16 requirements.txt added to study soft
    [P1-crt-results.csv]
2023-09-17 Trying to make FC work
    [P2-fc-results.csv]
2023-09-24 Added first proto PCB files
    [BOM_PCB_HapTID.csv, PickAndPlace_PCB_HapTID.csv]
2023-09-25 Fix PCB files
    [BOM_PCB_HapTID.csv, PickAndPlace_PCB_HapTID.csv]
2023-09-30 Added 3D models for prototype 1
    [flex_ring.3mf, flex_ring.step, wrist_motor_enclosure_bottom.3mf, wrist_motor_enclosure_bottom.step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]
2023-10-25 Updated prototype 1 3D models
    [electronics_enclosure_bottom.step, electronics_enclosure_button.step, electronics_enclosure_top.step, flex_ring.3mf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]
2023-11-14 Study progress
    [P1-crt-results.csv]
2024-02-21 New enclosure step files
    [electronics_enclosure_bottom_w_clips.step, electronics_enclosure_top_w_holes.step]
2024-03-03 Temp commit
    [P1-crt-results.csv, running_order_table.csv]
2024-03-13 Big unsaved study progress
    [running_order_table.csv]
2024-03-17 Study progress for pilot
    [running_order_table.csv, running_order_table_training.csv]
2024-03-25 Splitting the study in two
    [running_order.csv]
2024-04-04 Study part 1 progress
    [running_order_table_crt_training.csv]
2024-04-29 Study part 1 milestone
    [running_order.csv]
2024-04-30 Study part 1 final version
    [running_order.csv, running_order_table.csv, running_order_table_training.csv]
2024-05-23 Study part 2 progress
    [running_order.csv, running_order_crt_train.csv, running_order_table_crt_training.csv]
